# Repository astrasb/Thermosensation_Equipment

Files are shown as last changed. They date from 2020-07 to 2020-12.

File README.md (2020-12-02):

# Thermosensation Equipment
Repository collecting parts lists and wiring diagrams for custom nematode thermotaxis rigs and a thermal stimulator for calcium imaging of imobilized worms.

This respository includes two thermotaxis rig versions: 
1) a large format arena (22x22 cm assay area) capabile of generating temperatures from 12 - 46 degrees Celsius. This version was first described in [Bryant et al 2018].(https://www.sciencedirect.com/science/article/pii/S0960982218306997) It is an updated implementation of the arena described in the [Wormbook chapter on Thermotaxis Naviation Behavior (see section 5)] (http://www.wormbook.org/chapters/www_thermonav/thermonav.html) 
2) a small format arena (~7.6x5 cm assay arena) that can generate temperatures in the *C. elegans* physiological temperature range, and may be capable of warmer temperatures. This version is an updated implementation of the arena described by [Ramot et al 2018](http://dx.doi.org/10.1523/JNEUROSCI.2857-08.2008) and in the [Wormbook chapter on Thermotaxis Naviation Behavior (see section 2)] (http://www.wormbook.org/chapters/www_thermonav/thermonav.html) 

The thermal stimulator for calcium imaging is designed for use on an upright Zeiss microscope.

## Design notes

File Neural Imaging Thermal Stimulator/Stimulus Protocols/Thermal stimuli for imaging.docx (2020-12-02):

Designing Thermal Stimuli for Ca2+ Imaging

Astra Bryant, 11-22-19

Updated 12-2-20

Goal: design thermal stimuli that can be generated by the thermal imaging stimulator. Include both non-physiological stimuli and stimuli that recapitulate the thermosensory experience of a S. stercoralis iL3 engaging in temperature-driven behaviors.

For all stimuli, worms should be held at starting temperature for 5 minutes prior to the start of imaging.

Non-Physiological Stimuli

Based on stimulus protocols from the lab of Daniel Colon-Ramos.

Positive Thermotaxis Stimulus:

Temperature | Rise Time (s) | Hold Time (s) | °C/sec
23 | 10 | 60 | 0.2°C/s
17 | 60 | 120 | 0.1°C/s
40 | 230 | 120 | 0.1°C/s
23 | 66 | 60 | 0.25°C/s

Total time = 726 seconds or 12.1 minutes; use a 13 minute recording period

Negative Thermotaxis Stimulus:

Temperature | Rise Time (s) | Hold Time (s) | °C/sec
23 | 10 | 60 | 0.2°C/s
22 | 10 | 120 | 0.1°C/s
13 | 90 | 120 | 0.1°C/s
23 | 100 | 120 | 0.1°C/s

Total time = 630 seconds or 10.5 minutes; use a 13 minute recording period

Near-Fictive Stimuli

Positive Thermotaxis

Calculate change in temperature of each worm per second (divide temp per frame times 2), take the median to generate an average °C/second for each worm. Take the median again to get the value across worms.

- Using Switch Point Tracking worms (5 PT and 5 NT from worms placed at 23°C). Selecting only worms that do PT, ramp is 0.029°C/second.
- Using Steep Gradient worm tracks from Bryant et al 2018 – these are the ones that we used to quantify worm speed from 25-27°C, plus they’re plotted in Figure 1a. As calculated when worms are migrating from 25-34°C, the ramp is 0.0268°C/second.
- Use Tax-4 No Cas 9 worms from Bryant et al 2018 – these worms are placed near 30°C. The ramp is 0.0137°C/second.
- Using 29-41°C worm tracks from Bryant et al 2018, the average ramp is 0.0089°C/second for the whole range. From 29-37°C range, average ramp is 0.0127°C/second

Pseudofictive Positive Thermotaxis Stimulus:

Temperature | Rise Time (s) | Hold Time (s) | °C/sec
23 | 10 | 60 | 0.2°C/s
20 | 30 | 120 | 0.1°C/s
34 | 560 | 120 | 0.025°C/s
23 | 44 | 120 | 0.25°C/s

Total time = 1064 seconds or 17.73 minutes; use an 18 minute recording period

Pseudofictive Positive Thermotaxis Extended Stimulus:

Temperature | Rise Time (s) | Hold Time (s) | °C/sec
23 | 10 | 60 | 0.2°C/s
20 | 30 | 120 | 0.1°C/s
40 | 800 | 120 | 0.025°C/s
23 | 66 | 120 | 0.25°C/s

Total time = 1304 seconds or 21.73 minutes; use a 23 minute recording period

Negative Thermotaxis – NOT USED

Calculate change in temperature of each worm per second (divide temp per frame times 2), take the median to generate an average °C/second for each worm. Take the median again to get the value across worms.

- Using Switch Point Tracking worms (5 PT and 5 NT from worms placed at 23°C). Selecting only worms that do NT, ramp is -0.0055°C/second.

Fictive Negative Thermotaxis Stimulus:

Temperature | Rise Time (s) | Hold Time (s) | °C/sec
22 | 5 | 120 | 0.2°C/s
20 | 400 | 120 | 0.005°C/s
23 | 60 | 120 | 0.05°C/s

Total time = 830 seconds or 13.833 minutes

Reversal Behavior – NOT USED

Use the reversal behaviors observed in a 15-25°C gradient, Tc = 23°C. Defining PT as start of track to first time worms reach maxtemp-0.5°C. Defining NT zone as last time worms are at maxtemp-0.5°C to end of track. PT ramp = 0.0095°C/second. NT ramp = -0.0043°C/second.

- Time in PT = 158 sec
- Time @ maxtemp +/- 0.5°C = 262 sec
- Time in NT = 650 sec

Fictive Reversal Behavior Stimulus:

Temperature | Rise Time (s) | Hold Time (s) | °C/sec
23 | 10 | 60 | n/a
25 | 200 | 270 | 0.01°C/s
23 | 400 | 60 | 0.005°C/s

Total time = 1,000 seconds or 16 minutes and 40 seconds.

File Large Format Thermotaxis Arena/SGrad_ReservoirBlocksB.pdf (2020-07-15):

# MAKE 2

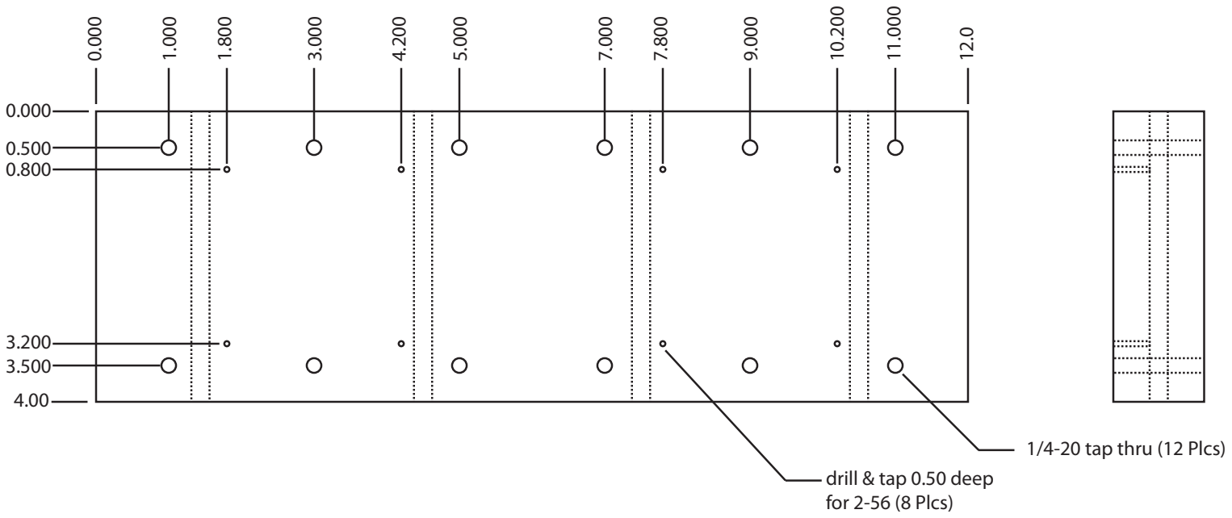
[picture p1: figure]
1/4-20 tap thru (12 Plcs); drill & tap 0.50 deep for 2-56 (8 Plcs)
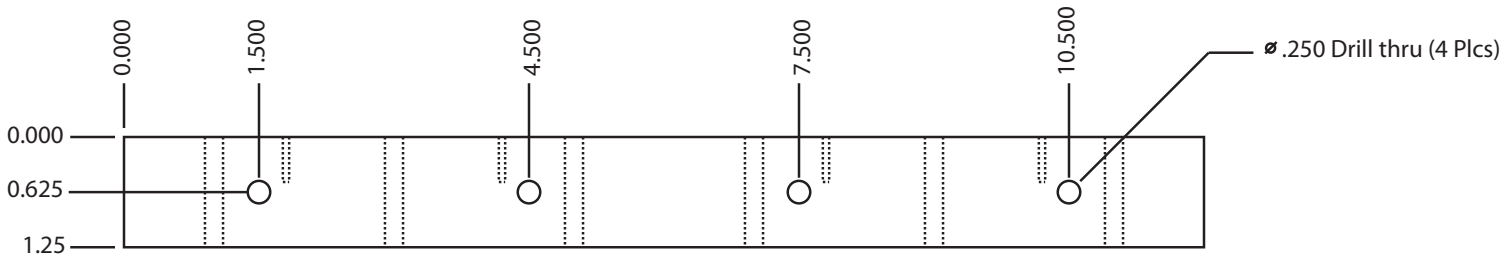
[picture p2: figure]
.250 Drill thru (4 Plcs)

SPATIAL GRADIENT RESERVOIR BLOCKS Make from Aluminum
Mason Klein, Harvard U.
09/30/2010

mklein@fas.harvard.edu, 617-496-5337 SCALE = 1:2

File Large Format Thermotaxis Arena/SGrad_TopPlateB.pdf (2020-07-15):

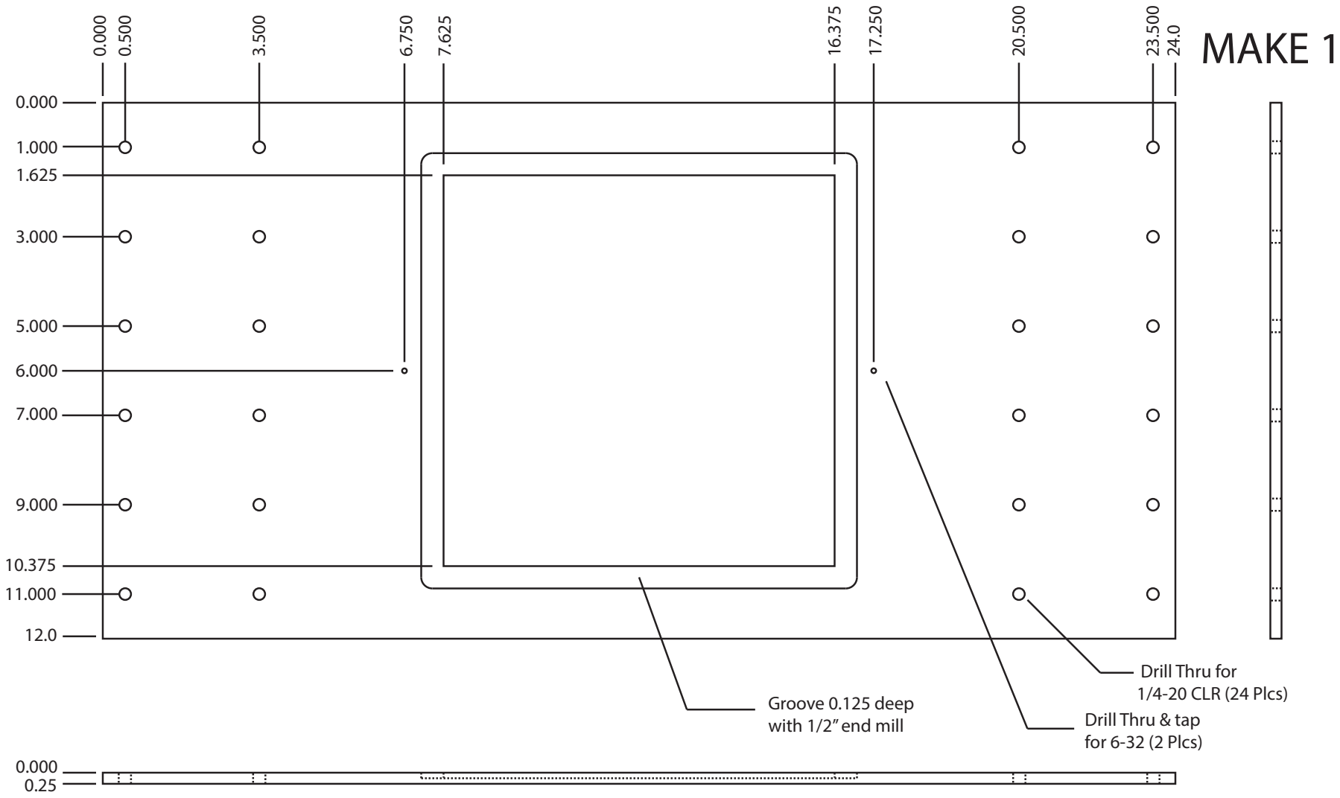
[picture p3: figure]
Drill Thru for 1/4-20 CLR (24 Plcs); MAKE 1; Drill Thru & tap for 6-32 (2 Plcs); Groove 0.125 deep with 1/2” end mill

SPATIAL GRADIENT TOP PLATE
Make from Aluminum, black anodized Mason Klein, Harvard U.
08/22/2011
mklein@fas.harvard.edu, 617-496-5337

# MUST BE ANODIZED (BLACK) SCALE = 1:3

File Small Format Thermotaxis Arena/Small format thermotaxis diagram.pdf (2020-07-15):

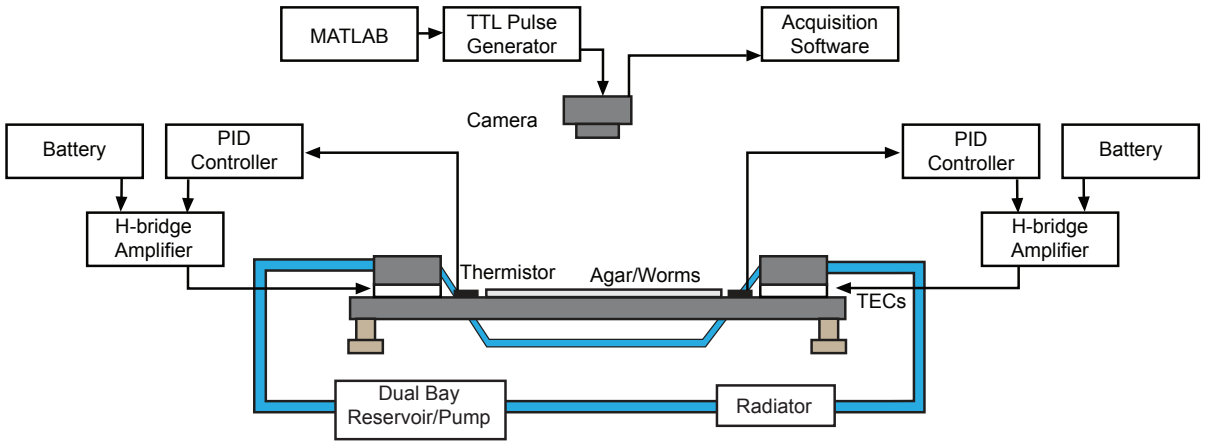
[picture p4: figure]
Camera; Thermistor; Agar/Worms; TECs; Acquisition Software; TTL Pulse Generator MATLAB; H-bridge Amplifier; Battery; PID; Controller; Battery PID Controller; Dual Bay; Reservoir/Pump; Radiator

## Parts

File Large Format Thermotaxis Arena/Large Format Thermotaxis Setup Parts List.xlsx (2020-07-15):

 | What is it doing? | Part-Number | Company | Description | Number of Items Per Setup | Cost per Item | Total Cost | Link
Peltier circuit components | Peltier circuit components
 | Instructions for wiring together the Peliter elements are provided by Accuthermo - see their installation guides.
 |  | FTX700D | Accuthermo | H-bridge amplifier | 2 | 99.00 | 198.00 | http://accuthermo.com/products_6.asp?pid=12420101032578117703
 |  | ATEC302 + URC-1020-BM | Accuthermo | TEC Temp controller with URC-1020-BM Serial to USB Interface Cable | 2 | 350.00 | 700.00 | http://accuthermo.com/products_5.asp?pid=10182009116534781386&pname=ATEC302+TEC+Temperature+Controller
 |  | LSMN-TR2252 | Accuthermo | Thermistor | 2 | 15.00 | 30.00 | https://www.mcmaster.com/6568t46
 |  | SP-320-12 | Oven Industries | Switching Power Supply | 2 | 95.45 | 190.90 | https://www.ovenind.com/product/power-supply-320w-12v/
 |  | MCTE1-19913L-S | Newark | Peliter heating elements | 4 | 44.00 | 176.00 | http://www.newark.com/multicomp/mcte1-19913l-s/thermoelectric-module-200w/dp/08P1466?ost=1639732
 |  | 3883K24 | McMaster Carr | Thermal Compound (optional, swiftech comes with thermal compound but if you replace the peltiers at any point you'll need some | 1 | 16.92 | 16.92 | https://www.mcmaster.com/3883k24
 | The 14 gauge wire carries the power to the peliters | 8054T17 | McMaster-Carr | 14 Gauge Stranded Wire (Red) 25 ft | 1 | 11.87 | 11.87 | https://www.mcmaster.com/8054t17
 |  | 8054T17 | McMaster-Carr | 14 Gauge Stranded Wire (Black) 25 ft | 1 | 11.87 | 11.87 | https://www.mcmaster.com/8054t17
 |  | 8280T32 | McMaster-Carr | 4-Wire 22 Gauge General Purpose Wire 10 ft | 1 | 7.87 | 7.87 | https://www.mcmaster.com/8280t32
 | Main body | 9995T91 | McMaster-Carr | Self-balancing mount feet 1/4"-20 thread | 4 | 5.36 | 21.44 | https://www.mcmaster.com/9995t91
 |  | 94335A151 | McMaster-Carr | Legs, 1" long, 3/4" wide, partially threaded for 1/4"-20 thread size | 4 | 5.36 | 21.44 | https://www.mcmaster.com/94335a151
 |  | 91792A537 | McMaster-Carr | 18-8 Stainless steel pan head slotted screws (pack of 50) (1/4"-20 thread, 1/2" long) | 1 | 7.23 | 7.23 | https://www.mcmaster.com/91792a537
 |  | 9434K23 | McMaster-Carr | Compression springs (as spacers on the screws that attach the swiftech waterblock to the metal plate) package of 5 | 4 | 4.85 | 19.40 | https://www.mcmaster.com/9434k23
 |  | A25093CT-ND | Digikey | AMP Connector (Gold Pins female 26-30 AWG) | 8 | 1.08 |  | https://www.digikey.com/product-detail/en/te-connectivity-amp-connectors/66424-8/A25093CT-ND/294702
 |  | A25088CT-ND | Digikey | AMP Connector (Gold Pins male - 26-30 AWG) | 8 | 0.97 |  | https://www.digikey.com/product-detail/en/te-connectivity-amp-connectors/66425-7/A25088CT-ND/294704
 | CUSTOM ITEM |  |  | Metal top plate and reservoir blocks
Coolant System | Coolant system
 |  | 5388K16 | McMaster-Carr | General purpose worm-drive clamps | 1 pack of 10 | 5.87 | 5.87 | https://www.mcmaster.com/5388k16
 |  | 5231K375 | McMaster-Carr | PVC tubing 1/2" ID, 3/4" OD | 25 ft |  |  | https://www.mcmaster.com/5231k375
 |  | 5385K25 | McMaster-Carr | Quick-disconnect tube for 1/2" ID (female) | 2 | 21.08 | 42.16
 |  | 5385K55 | McMaster-Carr | Quick-disconnect tube for 1/2" ID (male) | 2 | 16.42 | 32.84
 |  | 13-874-180 | Fisher Scientific | Isotemp Refrigetated/Heated Circulating Water Bath (exact version not necessary, just needs to hold temps between 0 and at least 60C) | 1 pack of 10 | 1900 | 1900
 |  | MCW820 | Switfech | Swiftech MCW-Ramcool/A VGA Memory Waterblock | 2 | 56.95 | 113.90 | http://www.swiftech.com/mcw82vgawaterblock.aspx
Video Imaging | Video Imaging
 | LED lighting Array for video imaging |  | Amazon | Chip-on-board Red LED strips |  |  |  | https://www.amazon.com/YINTATECH-Universal-Waterproof-Daytime-Running/dp/B075XM4SLZ?s=aps
 |  |  | Target? Amazon? | Picture frame to mount the LED strips on - size depends on size of plate, should be big enough to completely surround the agar plate (fits in between the agar plate and the swiftechs. If possible, use a metal one that can act as a heat sink for the LED strips.
 |  | MW122A | Amazon | LED power supply | 1 | 45.50 | 45.50 | https://www.amazon.com/Philmore-Multi-Voltage-Regulated-Power-Supply/dp/B004M45MHQ
 |  | BTE-BO5O-U | Mightex Systems | Buffered 5 MP 12-bit monochrome CMOS camera, enclosed | 1 | 389.00 | 389.00 | https://secure.mightexsystems.com/family_info.php?cPath=285_1_251_170_101&categories_id=101
 |  | ACC-CAM-DIN8 | Mightex Systems | CCD Camera cable with 8-pin DIN connector | 1 | 12.00 | 12.00 | https://www.mightexsystems.com/family_info.php?cPath=95_39_40&categories_id=40
 |  | M0814-MP | Mightex Systems | Comptar 2/3" 8mm Megapixel lens with manuel iris | 1 | 165.00 | 165.00 | https://secure.mightexsystems.com/family_info.php?cPath=285_78_79_81&categories_id=81
 |  | 8054T31 | McMaster-Carr | 28 Gauge Stranded Wire (Red) 25ft | 1 | 2.82 | 2.82 | https://www.mcmaster.com/8054T31
 |  | 8054T31 | McMaster-Carr | 28 Gauge Stranded Wire (Brown) 25ft | 1 | 2.82 | 2.82 | https://www.mcmaster.com/8054T31
 |  | U3-LV | LabJack Corporation | Low cost device for generating TTL pulses (for triggering cameras) | 1 | 108.00 | 108.00 | https://labjack.com/products/u3
 |  |  | Mathworks | Matlab student license | 1 | 49.00 | 49.00
 |  |  | Amazon | Cabinet for housing the setup - you'll need it to be dark for the dark-light illumination to work. | 1 | 140.69 | 140.69 | https://www.amazon.com/dp/B0166R5ZRS
 |  |  |  | Misc equipment for mounting camera in the cabinet
 | Process Camera Images into X/Y coordinates using FIJI, then quantify X/Y coordinates using Matlab |  |  | Matlab code avaliable on Github: https://github.com/HallemLab/FIJI_Scripts and https://github.com/HallemLab/Thermotaxis_Tracker
 | Trigger Camera Acquisition |  |  | Matlab code for triggering camera acqusition avaliable on Github: https://github.com/HallemLab/Labjack_Camera_Trigger
Misc Equipment + Consumables | Misc Equipment + Consumables
 |  |  | Soldering iron
 |  |  | Resin core solder
 |  |  | Screwdrivers, all sorts
 |  | 3883K24 | McMaster Carr | Thermal Compound (optional, swiftech comes with thermal compound but if you replace the peltiers at any point you'll need some | 1 | 16.92 | 16.92 | https://www.mcmaster.com/3883k24
 |  |  | Assay plates | Corning™ 245mm Square BioAssay Dishes | At least 1 case - 2 is better | $89.28 (per case) |  | http://www.fishersci.com/ecomm/servlet/fsproductdetail?storeId=10652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
 |  |  | Materials for thermotaxis agar | see Bryant et al 2018 for recipie for 3% thermotaxis agar; also Wormbook
 |  |  | Amazon | Laser thermometer | 1 | 15.99 | 15.99 | https://www.amazon.com/Etekcity-Lasergrip-774-Non-contact-Thermometer/dp/B00837ZGRY?s=industrial
 |  |  |  | Glycerol - as a thermal conductor between metal of the plate and the bottom of the assay plate - I use ~70% (mix 100% with water)
 |  |  |  | Sticky putty/tape for attaching the thermosistor to the plate

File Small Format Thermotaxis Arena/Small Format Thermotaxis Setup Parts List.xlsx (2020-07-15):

 | What is it doing? | Part-Number | Company | Description | Number of Items Per Setup | Cost per Item | Total Cost | Link
Peltier circuit components | Peltier circuit components
 | Instructions for wiring together the Peliter elements are provided by Accuthermo - see their installation guides.
 |  | FTX700D | Accuthermo | H-bridge amplifier | 2 | 99.00 | 198.00 | http://accuthermo.com/products_6.asp?pid=12420101032578117703
 |  | ATEC302 + URC-1020-BM | Accuthermo | TEC Temp controller with URC-1020-BM Serial to USB Interface Cable | 2 | 350.00 | 700.00 | http://accuthermo.com/products_5.asp?pid=10182009116534781386&pname=ATEC302+TEC+Temperature+Controller
 |  | LSMN-TR2252 | Accuthermo | Thermistor | 2 | 15.00 | 30.00 | https://www.mcmaster.com/6568t46
 |  | SP-320-12 | Oven Industries | Switching Power Supply | 2 | 95.45 | 190.90 | https://www.ovenind.com/product/power-supply-320w-12v/
 |  | MCTE1-19913L-S | Newark | Peliter heating elements | 2 | 44.00 | 88.68 | http://www.newark.com/multicomp/mcte1-19913l-s/thermoelectric-module-200w/dp/08P1466?ost=1639732
 |  | 3883K24 | McMaster Carr | Thermal Compound (optional, swiftech comes with thermal compound but if you replace the peltiers at any point you'll need some | 1 | 16.92 | 16.92 | https://www.mcmaster.com/3883k24
 | The 14 gauge wire carries the power to the peliters | 8054T17 | McMaster-Carr | 14 Gauge Stranded Wire (Red) 25 ft | 1 | 11.87 | 11.87 | https://www.mcmaster.com/8054t17
 |  | 8054T17 | McMaster-Carr | 14 Gauge Stranded Wire (Black) 25 ft | 1 | 11.87 | 11.87 | https://www.mcmaster.com/8054t17
 |  | 8280T32 | McMaster-Carr | 4-Wire 22 Gauge General Purpose Wire 10 ft | 1 | 7.87 | 7.87 | https://www.mcmaster.com/8280t32
 | Main body | 9995T91 | McMaster-Carr | Self-balancing mount feet 1/4"-20 thread | 4 | 5.36 | 21.44 | https://www.mcmaster.com/9995t91
 |  | 94335A151 | McMaster-Carr | Legs, 1" long, 3/4" wide, partially threaded for 1/4"-20 thread size | 4 | 5.36 | 21.44 | https://www.mcmaster.com/94335a151
 |  | 91792A537 | McMaster-Carr | 18-8 Stainless steel pan head slotted screws (pack of 50) (1/4"-20 thread, 1/2" long) | 1 | 7.23 | 7.23 | https://www.mcmaster.com/91792a537
 |  | 9434K23 | McMaster-Carr | Compression springs (as spacers on the screws that attach the swiftech waterblock to the metal plate) package of 5 | 2 | 4.85 | 9.70 | https://www.mcmaster.com/9434k23
 |  | A25093CT-ND | Digikey | AMP Connector (Gold Pins female 26-30 AWG) | 4 | 1.08 |  | https://www.digikey.com/product-detail/en/te-connectivity-amp-connectors/66424-8/A25093CT-ND/294702
 |  | A25088CT-ND | Digikey | AMP Connector (Gold Pins male - 26-30 AWG) | 4 | 0.97 |  | https://www.digikey.com/product-detail/en/te-connectivity-amp-connectors/66425-7/A25088CT-ND/294704
 | CUSTOM ITEM |  |  | Metal plate, for specs see Thermal Gradient Plate 10"x5"x1/8".pdf; Alternatively, take a metal plate with the same dimensions and glue appropriately sized screw nuts in the locations where the screw holes for attaching the waterblock are located.
Coolant System | Coolant system
 |  | 5388K14 | McMaster-Carr | General purpose worm-drive clamps | 1 pack of 10 | 5.87 | 5.87
 |  | 441802-HE-80882 | McMaster-Carr | Masterkleer PVC tubing 3/8" ID, 1/2" OD | 25 ft |  | 8.75
 | The 3/8" diameter PVC tubing may be slightly too narrow to comfortably fit on the barb fittings that come with the Swiftech waterblock. These should fit well as replacements if necessary (2 per swiftech waterblock). You'll also need 2 for the reservoir/pump combo (see below). A total of 6 are probably necessary. |  | Amazon | XPSC G1/4" to 3/8" barb fitting black chrome, 4 pack | 2 | 8.05 | 16.1 | https://www.amazon.com/XSPC-Barb-Fitting-Black-Chrome/dp/B00NODEEBQ?srs=8272996011
 |  | MCW820 | Switfech | Swiftech MCW-Ramcool/A VGA Memory Waterblock | 2 | 56.95 | 113.90 | http://www.swiftech.com/mcw82vgawaterblock.aspx
 | These are sized for working with the XSPC reservoir/pump | 5923K44 | McMaster-Carr | Quick-disconnect tube coupling for food and beverage for 3/8" ID tubing (female) | 2 | 9.86 | 19.72 | https://www.mcmaster.com/5923k44
 |  | 5923K74 | McMaster-Carr | Quick-disconnect tube coupling for food and beverage for 3/8" ID tubing (male) | 2 | 9.76 | 19.52 | https://www.mcmaster.com/5923K74
 |  |  | Amazon | XSPC Twin D5 Dual Bay Reservoir/Pump Combo (SATA Power) | 1 | 229.99 | 229.99 | https://www.amazon.com/gp/product/B074G42N72/ref=s9_dcacsd_dcoop_bw_c_x_2_w
 |  |  | Amazon | AGPtek® 12 Pipe Aluminum Heat Exchanger Radiator for PC CPU CO2 Laser Water Cool System Computer | 1 | 16.99 | 16.99 | https://www.amazon.com/AGPtek%C2%AE-Aluminum-Exchanger-Radiator-Computer/dp/B00CFDS3JA?s=industrial&dpID=51rhpxdBbHL&preST=_SY300_QL70_&dpSrc=srch
 | Alternatively, rip one out of an old computer. You'll need to short the power supply in order for it to turn on without being plugged in to a motherboard. I used a thick paperclip, although you could do something fancier like a thick wire or a switch. There are instructions on the web. For example, see steps 3-6: https://www.wikihow.com/Check-a-Power-Supply |  | Amazon | SATA power source for a computer to run the pump | 1 | 40.00 | 40.00 | https://www.amazon.com/HPC-430-N12S-Intel-Approved-low-noise-performance-PCI-EXPRESS/dp/B000VN1ZK0?s=electronics
 | Alternative to the paperclip method |  | Amazon | CRJ 24-Pin ATX Red LED Power On/Off Switch Jumper Bridge Cable, Black Sleeved 22" | 1 | 8.99 | 8.99 | https://www.amazon.com/CRJ-24-Pin-Switch-Jumper-Sleeved/dp/B01MSY4966
 | If you have an extra computer power cable lying around, you could use that too. |  | Amazon | Power cable for SATA power source | 1 | 4.99 | 4.99 | https://www.amazon.com/AmazonBasics-Power-Cord-3-Foot-Black/dp/B072BYGKZW?s=electronics
Video Imaging | Video Imaging
 | LED lighting Array for video imaging |  | Amazon | Chip-on-board Red LED strips |  |  |  | https://www.amazon.com/YINTATECH-Universal-Waterproof-Daytime-Running/dp/B075XM4SLZ?s=aps
 |  |  | Target? Amazon? | Picture frame to mount the LED strips on - size depends on size of plate, should be big enough to completely surround the agar plate (fits in between the agar plate and the swiftechs. If possible, use a metal one that can act as a heat sink for the LED strips.
 |  | MW122A | Amazon | LED power supply | 1 | 45.50 | 45.50 | https://www.amazon.com/Philmore-Multi-Voltage-Regulated-Power-Supply/dp/B004M45MHQ
 |  | BTE-BO5O-U | Mightex Systems | Buffered 5 MP 12-bit monochrome CMOS camera, enclosed | 1 | 389.00 | 389.00 | https://secure.mightexsystems.com/family_info.php?cPath=285_1_251_170_101&categories_id=101
 |  | ACC-CAM-DIN8 | Mightex Systems | CCD Camera cable with 8-pin DIN connector | 1 | 12.00 | 12.00 | https://www.mightexsystems.com/family_info.php?cPath=95_39_40&categories_id=40
 |  | M0814-MP | Mightex Systems | Comptar 2/3" 8mm Megapixel lens with manuel iris | 1 | 165.00 | 165.00 | https://secure.mightexsystems.com/family_info.php?cPath=285_78_79_81&categories_id=81
 |  | 8054T31 | McMaster-Carr | 28 Gauge Stranded Wire (Red) 25ft | 1 | 2.82 | 2.82 | https://www.mcmaster.com/8054T31
 |  | 8054T31 | McMaster-Carr | 28 Gauge Stranded Wire (Brown) 25ft | 1 | 2.82 | 2.82 | https://www.mcmaster.com/8054T31
 |  | U3-LV | LabJack Corporation | Low cost device for generating TTL pulses (for triggering cameras) | 1 | 108.00 | 108.00 | https://labjack.com/products/u3
 |  |  | Mathworks | Matlab student license | 1 | 49.00 | 49.00
 |  |  | Amazon | Cabinet for housing the setup - you'll need it to be dark for the dark-light illumination to work. | 1 | 140.69 | 140.69 | https://www.amazon.com/dp/B0166R5ZRS
 |  |  |  | Equipment for mounting camera in the cabinet
 | Process Camera Images into X/Y coordinates using FIJI, then quantify X/Y coordinates using Matlab |  |  | Matlab code avaliable on Github: https://github.com/HallemLab/FIJI_Scripts and https://github.com/HallemLab/Thermotaxis_Tracker
 | Trigger Camera Acquisition |  |  | Matlab code for triggering camera acqusition avaliable on Github: https://github.com/HallemLab/Labjack_Camera_Trigger
Misc Equipment + Consumables | Misc Equipment + Consumables
 |  |  | Soldering iron
 |  |  | Resin core solder
 |  |  | Screwdrivers, all sorts
 |  | 3883K24 | McMaster Carr | Thermal Compound (optional, swiftech comes with thermal compound but if you replace the peltiers at any point you'll need some | 1 | 16.92 | 16.92 | https://www.mcmaster.com/3883k24
 |  |  | Assay plates | vented, rectangular assay plates (7.6 cm l x 5 cm w x 1 cm d, LabScientific, Livingston, NJ) (source: Wormbook)
 |  |  | Materials for thermotaxis agar | see Bryant et al 2018 for recipie for 3% thermotaxis agar; also Wormbook
 |  |  | Amazon | Laser thermometer | 1 | 15.99 | 15.99 | https://www.amazon.com/Etekcity-Lasergrip-774-Non-contact-Thermometer/dp/B00837ZGRY?s=industrial
 |  |  |  | Glycerol - as a thermal conductor between metal of the plate and the bottom of the assay plate - I use ~70% (mix 100% with water)
 |  |  |  | Sticky putty/tape for attaching the thermosistor to the plate

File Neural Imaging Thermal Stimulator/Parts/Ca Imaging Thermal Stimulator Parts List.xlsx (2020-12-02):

 | What is it doing? | Part-Number | Company | Description | Number of Items Per Setup | Cost per Item | Total Cost | Link
Peltier circuit components | Peltier circuit components
 | Instructions for wiring together the Peliter elements are provided by Accuthermo - see their installation guides.
 |  |  | DigiKey | AC/DC CONVERTER 12V 35W | 2 | 21.14 | 42.28 | http://www.digikey.com/product-detail/en/tdk-lambda-americas-inc/LS35-12/285-1891-ND/2057040
 | Peliter with an anulus |  | DigiKey | PELTIER SH10,95,06,L,RT,W12 | 1 | 58.18 | 58.18 | http://www.digikey.com/product-search/en?mpart=430533-502&vendor=1487
 |  |  | DigiKey | CORD 18AWG 3COND 79" BLACK SVT | 1 | 4 | 4 | http://www.digikey.com/product-detail/en/311007-01/Q106-ND/183390
 |  | 8280T32 | McMaster | 4-wire 22 gauge general purpose cable, 10 ft | 1 | 7.87 | 7.87 | http://www.mcmaster.com/#8280t32/=12l0n4x
 |  | FTX700D | Accuthermo | H-bridge amplifier | 1 | 99.00 | 99 | http://accuthermo.com/products_6.asp?pid=12420101032578117703
 |  | ATEC302 + URC-1020-BM | Accuthermo | TEC Temp controller with URC-1020-BM Serial to USB Interface Cable | 1 | 350.00 | 350 | http://accuthermo.com/products_5.asp?pid=10182009116534781386&pname=ATEC302+TEC+Temperature+Controller
 |  | 43AC9645 | Newark | USP12837 - Thermistor, NTC, Probe, 10 kohm, 1%, Polyamide, Wire Leaded | 5 | 19 | 95 | https://www.newark.com/littelfuse/usp12837/ntc-thermistor-10k-wire-leaded/dp/43AC9645
 |  | 92F8438 | Newark | Multimate, Type III+ Series, Pin, Crimp, 14 AWG, Gold Plated Contacts | 10 | 0.715 | 7.15 | https://www.newark.com/amp-te-connectivity/66361-3/contact-pin-18-14awg-crimp/dp/92F8438?st=gold%20pins
 |  | 54H3461 | Newark | Multimate, Type III+ Series, Socket, Crimp, 14 AWG, Gold Plated Contacts | 10 | 1.12 | 11.2 | https://www.newark.com/amp-te-connectivity/66360-4/contact-socket-18-14awg-crimp/dp/54H3461?st=66360-4
 | CUSTOM ITEM |  |  | 3D printed stage clamp
 | CUSTOM ITEM |  |  | Aluminum heat block with recessed slot for peltier
Coolant System | Coolant system
 |  | 5121K181 | McMaster | 1/2" ID Tube-to-tube connectors | 1 | 4.62 | 4.62 | https://www.mcmaster.com/#5121K181
 |  | 51205K176 | McMaster | 1/8" NPT extreme pressure stainless steel plug | 1 | 7.15 | 7.15 | https://www.mcmaster.com/#51205K176
 |  | 44555K131 | McMaster | 1/8" NPT tube-to-male threaded pipe (1/8" to 1/4") | 2 | 2.31 | 4.62 | https://www.mcmaster.com/#44555K131
 |  | 5388K17 | McMaster | General purpose worm-drive clamps (1/2 to 29/32") | 1 | 6.45 | 6.45 | https://www.mcmaster.com/#5388K17
 |  | 5388K14 | McMaster | General purpose worm-drive clamps (7/32 - 5/8") | 2 | 5.87 | 11.74 | https://www.mcmaster.com/#5388K14
 |  | 5113K35 | McMaster | Low-Temperature EVA Tubing, 25 ft | 1 | 0.44 | 0.44 | http://www.mcmaster.com/#5113K35
 |  | 5923K74 | McMaster | Male Barbed Tube Quick-Disconnect With Shutoff, 3/8 tube ID | 2 | 9.76 | 19.52 | http://www.mcmaster.com/#5923K74
 |  | 5923K43 | McMaster | Female Barbed Tube Socket Quick Disconnect with Shutoff, 1/4 tube ID | 2 | 9.86 | 19.72 | https://www.mcmaster.com/#5923K43
 |  | 13-874-180 | Fisher Scientific | Fisherbrand™ Isotemp™ Refrigerated/Heated Bath Circulators: 5.4-6.5L, 115V/60Hz | 1 | 1900 | 1900 | https://www.fishersci.com/shop/products/fisher-scientific-isotemp-refrigerated-heated-bath-circulators-5-4-6-5l-115v-60hz-4/13874180?searchHijack=true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

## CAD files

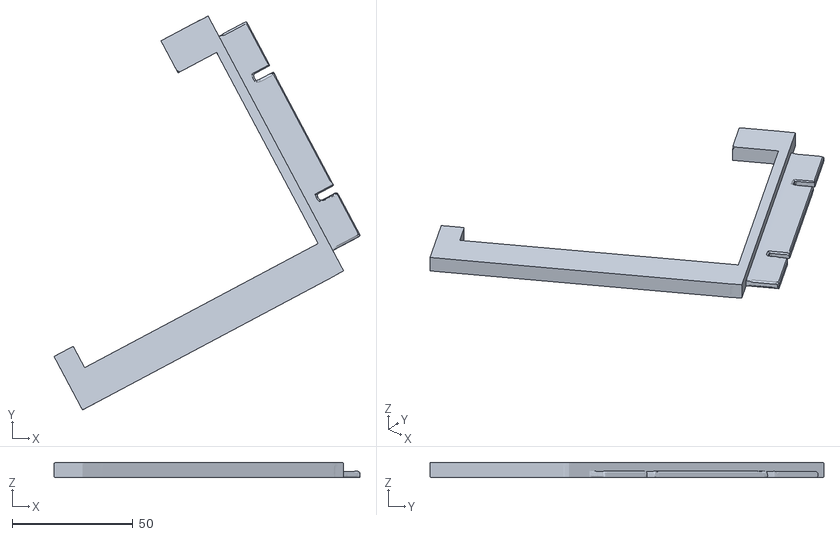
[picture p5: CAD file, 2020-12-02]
Neural Imaging Thermal Stimulator/Custom Stage Clamp/thermal baseplate v5.stl
127.0 x 163.5 x 6.04

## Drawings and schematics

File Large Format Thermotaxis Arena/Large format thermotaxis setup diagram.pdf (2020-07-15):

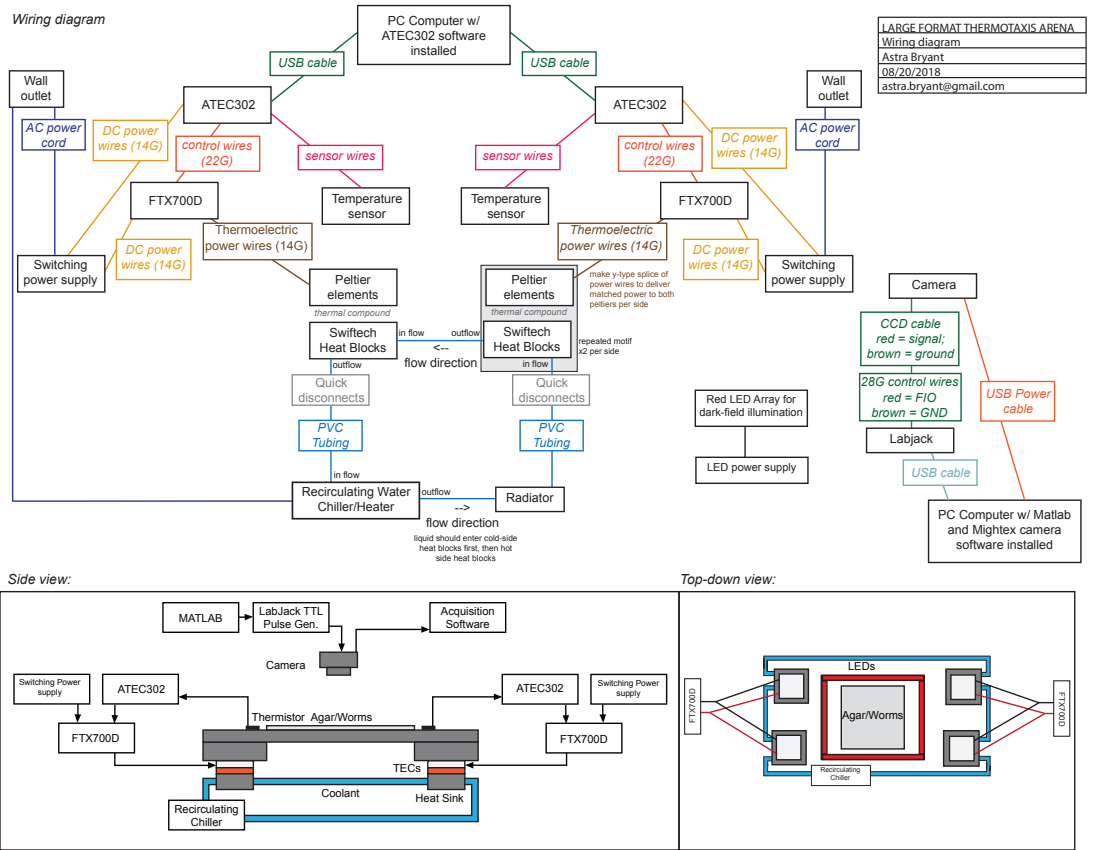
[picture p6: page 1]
Temperature sensor; Wall outlet; Peltier elements; Thermoelectric power wires (14G); USB cable; AC power cord; sensor wires; control wires (22G); DC power wires (14G); Swiftech Heat Blocks; PVC Tubing; flow direction; in flow; outflow; Quick disconnects; thermal compound; PC Computer w/ ATEC302 software installed; FTX700D; Switching power supply; CCD cable red = signal; brown = ground; USB Power cable; Camera; 28G control wires red = FIO brown = GND; Labjack; Acquisition Software; LabJack TTL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

Wiring diagram
Astra Bryant
astra.bryant@gmail.com

make y-type splice of
power wires to deliver
matched power to both
peltiers per side

Red LED Array for
dark-field illumination

LED power supply

outflow
Radiator -->
flow direction
liquid should enter cold-side
heat blocks first, then hot
side heat blocks

PC Computer w/ Matlab
and Mightex camera
software installed

Pulse Gen. MATLAB

Thermistor Agar/Worms

Heat Sink Coolant

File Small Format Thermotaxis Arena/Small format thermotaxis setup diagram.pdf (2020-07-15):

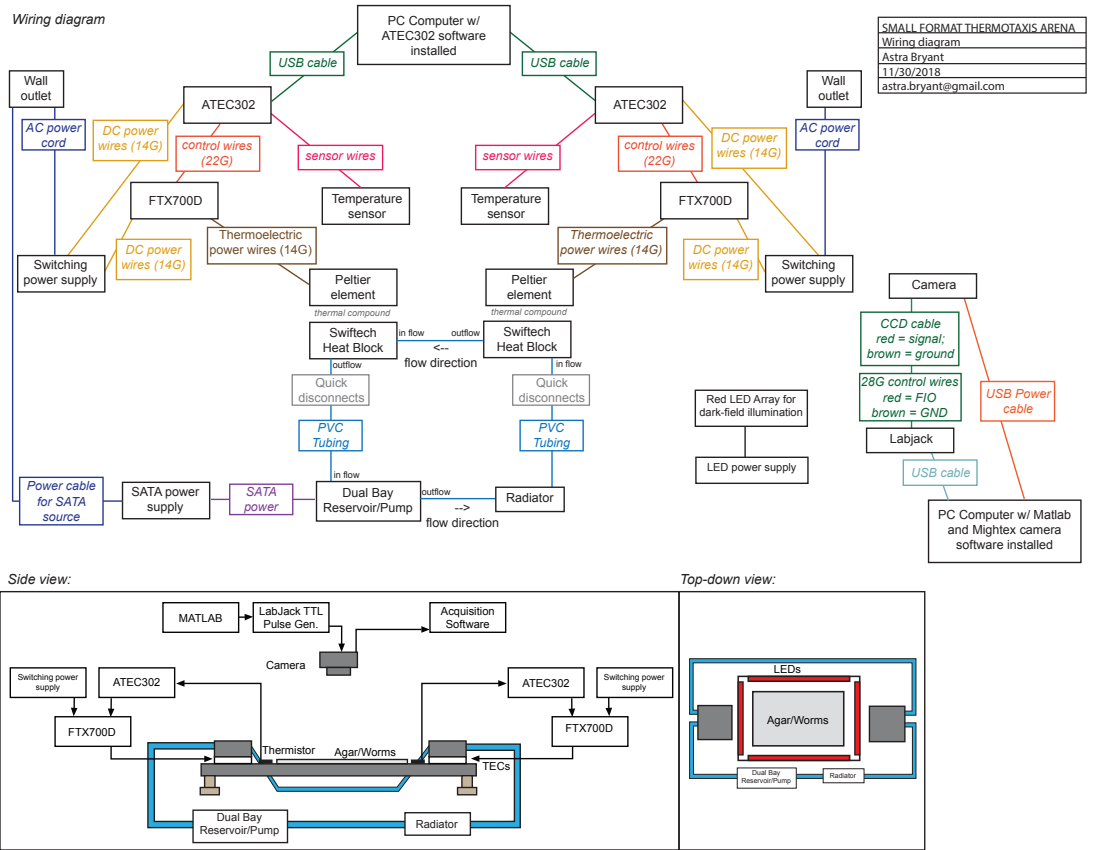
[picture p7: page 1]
Temperature sensor; Wall outlet; Peltier element; Thermoelectric power wires (14G); USB cable; AC power cord; sensor wires; control wires (22G); DC power wires (14G); Swiftech Heat Block; PVC Tubing; Dual Bay Reservoir/Pump; Radiator SATA power; SATA power supply; Power cable for SATA; source; flow direction; in flow; outflow; Quick disconnects; thermal compound; PC Computer w/ ATEC302 software installed; FTX700D; Switching power supply; CCD cable red = signal; brown = ground; USB Power cable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

Wiring diagram
Astra Bryant
astra.bryant@gmail.com

Red LED Array for
dark-field illumination

LED power supply

PC Computer w/ Matlab
and Mightex camera
software installed

Pulse Gen. MATLAB

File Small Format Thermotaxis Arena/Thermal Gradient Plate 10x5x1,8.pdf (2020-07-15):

10” x 5” x 1/8”

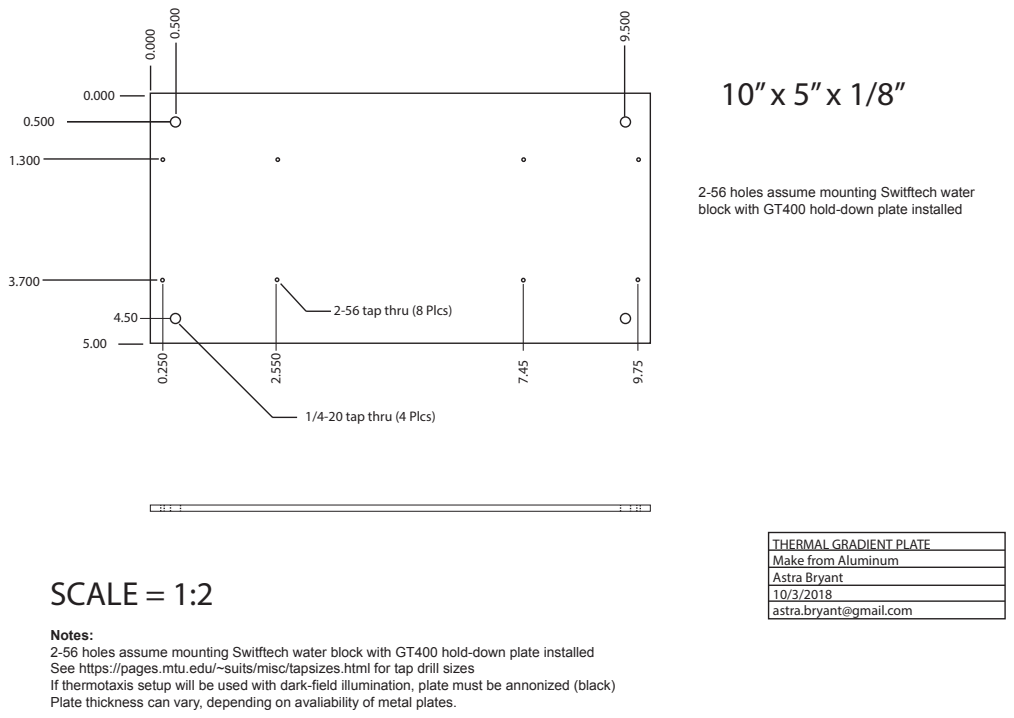
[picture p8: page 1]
SCALE = 1:2

2-56 holes assume mounting Switftech water
block with GT400 hold-down plate installed

2-56 tap thru (8 Plcs)

1/4-20 tap thru (4 Plcs)

THERMAL GRADIENT PLATE
Make from Aluminum
Astra Bryant
astra.bryant@gmail.com

Notes:
2-56 holes assume mounting Switftech water block with GT400 hold-down plate installed
See https://pages.mtu.edu/~suits/misc/tapsizes.html for tap drill sizes
If thermotaxis setup will be used with dark-field illumination, plate must be annonized (black)
Plate thickness can vary, depending on avaliability of metal plates.

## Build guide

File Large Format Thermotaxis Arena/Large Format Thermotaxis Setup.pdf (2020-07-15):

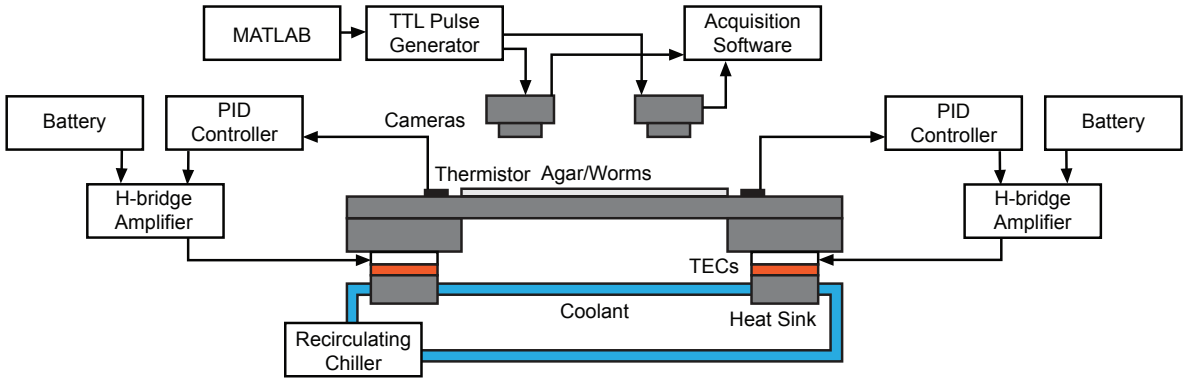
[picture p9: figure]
Cameras; Thermistor Agar/Worms; Heat Sink Coolant; TECs; H-bridge Amplifier; Battery PID Controller; Acquisition Software; TTL Pulse Generator MATLAB; Battery; PID; Controller; Recirculating Chiller

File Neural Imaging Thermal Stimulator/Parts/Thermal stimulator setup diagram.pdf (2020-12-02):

Temperature
sensor

Wall
outlet

Peltier
element

USB cable

AC power
cords
sensor wires

control wires
(22G)

DC power
wires (18G)

Thermoelectric
power wires (18G)

Custom Aluminum
Heat Block

PVC
Tubing

PVC
Tubing

outflow in flow
Quick
disconnects

Quick
disconnects

PC Computer w/
ATEC302 software
installed

FTX700D

DC power
wires (18G)
Wiring diagram | CALCIUM IMAGING THERMAL STIMULATOR
| Wiring diagram Astra Bryant 12/3/2020 astra.bryant@gmail.com

ATEC302

Recirculating Water
Chiller/Heater

peltier mounts into recess on heat block

Switching
power supply

Switching
power supply

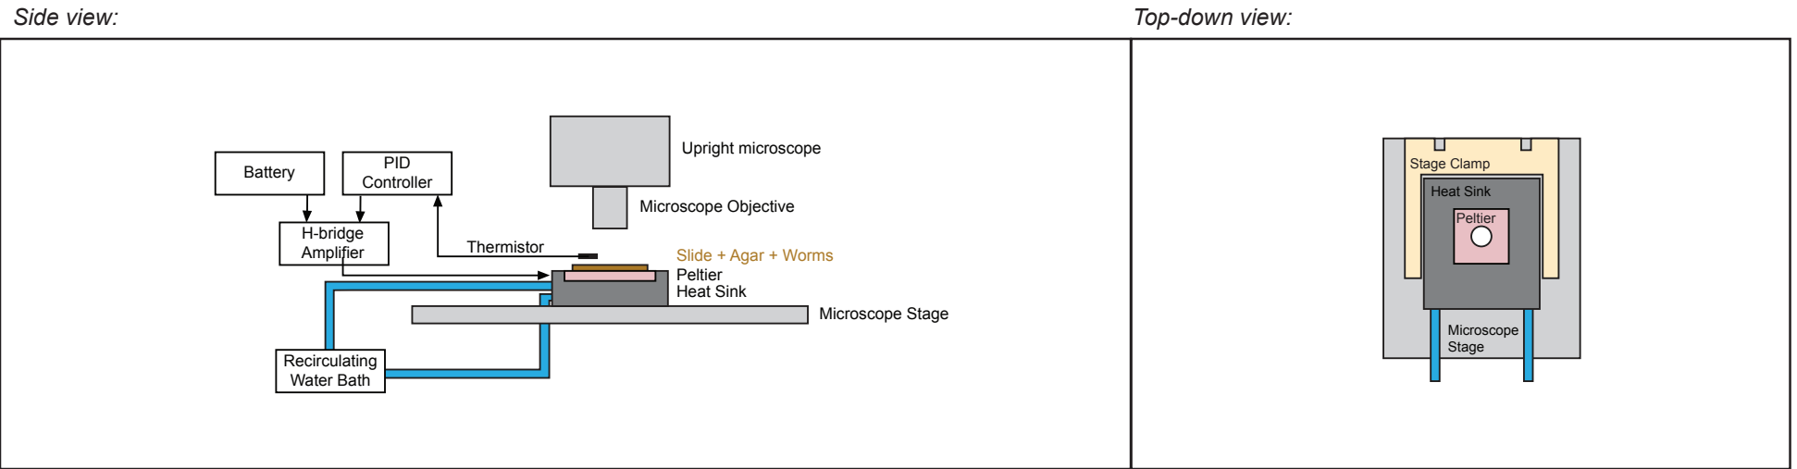
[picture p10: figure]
Side view:; Top-down view:; Recirculating Water Bath; Thermistor; Slide + Agar + Worms; Heat Sink; Peltier; Battery; PID; Controller; Microscope Stage; Microscope Objective; Upright microscope; H-bridge Amplifier; Heat Sink Peltier; Stage Clamp

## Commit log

2020-07-15 Initial Upload of Arena Setup
    Initial upload of parts lists and wiring diagrams for both large and small format thermotaxis arenas
    [Large Format Thermotaxis Setup Parts List.xlsx, Small Format Thermotaxis Setup Parts List.xlsx]
2020-07-15 Updated Large Format Parts list
    Now includes isotemp water bath
    [Large Format Thermotaxis Setup Parts List.xlsx]
